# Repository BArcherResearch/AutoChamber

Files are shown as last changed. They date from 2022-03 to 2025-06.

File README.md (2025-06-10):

# AutoChamber 

Follow "AutoChamber/Chamber_1/Build_Guide/Chamber.1 Build guide" to find the chamber build guide.

## Building an open-source community around the development and application of automatically ventilating floating greenhouse gas flux chambers. 

My name is ***** and I am currently a doctoral candidate working with *********

My research focus is greenhouse gas dynamics from freshwater bodies. In particular, the development of opensource technical solutions for the collection of GHG flux data over higher temporal and spatial resolutions than has typically been achievable with floating chamber methods, or without extensive engineering experience. 

The goal of this project is to provide all the information required for people, even those with little to no experience in 3d printing or the arduino environment, to be able to build a standardised automatically ventilating floating chamber system, capable of collecting GHG flux data of a quality suitable for publication. 

In doing so, the project aims to enhance the resolution of the global freshwater GHG budget by offering a solution that aligns with the philosophy and popularity of the floating chamber method—being low-cost, easily transportable and deployable, and requiring minimal construction skills.

By using 3d printing and universally available parts, the system aims to be standardised between research groups, eliminating the time investment, engineering skills and unrepeatability that often come with lab builds.

Developing the optimal system for these grand goals is an iterative and collaborative process. But with the release of "Chamber_1" as a part of my doctoral thesis, I hope to inspire the community and conversation around automatically ventilating chamber standardisation, and provide a case for what openSource science can achieve. 

## A note for those anxious about the 3d printing element of this project

If there is enough interest in the "Chamber_1" design or future designs/iterations, 3d printing (and thus subsequent post printing epoxy sealing steps) could be avoided or reduced by investing in injection moulding moulds and providing some of the parts as a kit; for example the main body and lid. 

This approach has been employed successfully by other opensource projects such as the "snowcat" by rctestflight (https://www.kickstarter.com/projects/164488684/r-c-snowcat-tracks-rctestflight). Not only does this approach save lots of time that would otherwise be taken by printing, but also it reducing the cost of the individual parts (after the moulds have been funded of course) and ensuring the gas tight nature of the design. 

In the mean time, the cost of 3d printing has been taken into account by basing the build of Chamber_1 around the most economic FDM style printer available on the market at the time of publication, the **anycubic chiron**.

Additionally, the rise of consumer based 3d printers means that many universities and Maker spaces now have 3d printing facilities that students can utilise.

However if this is still not a possibility or to your taste, low cost **3d printing services** are now offered by external companies such as JLCpcb. By simply providing the projects stl files, you can have your parts printed and delivered.

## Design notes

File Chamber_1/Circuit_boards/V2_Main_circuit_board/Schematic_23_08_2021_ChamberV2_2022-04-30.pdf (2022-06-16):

A | A
B | B
C | C
D | D
E | E
F | F
G | G
H | H

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
TITLE: Automatic GHG Chamber schematic version 2
REV: 1.0

Date: 23-08-2021

Sheet: 1/1
Drawn By:

Company: IGB-Berlin

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
GND GND

GND

10K

R14

1K for Q3 or 2.2k for Q15
R20

1K

R21

10K

R22

100nF

C5

100nF

C6

22pF

C7 | 22pF C8

SN74HC595DR

U7

QB 1
QC 2
QD 3
QE 4
QF 5
QG 6
QH 7
GND 8 | QH# 9

SRCLR# 10 SRCLK 11 RCLK 12 OE# 13 SER 14 QA 15 VCC 16

SN74HC595DR

U8

QB 1
QC 2
QD 3
QE 4
QF 5
QG 6
QH 7
GND 8 | QH# 9

SRCLR# 10 SRCLK 11 RCLK 12 OE# 13 SER 14 QA 15 VCC 16

MMBT2222A_C400799

Q1

+5V

MMBT2222A_C400799

Q3 | GND

PD6

Servo Connector

Optical interrupt Connector

+5V

1K

R24

MMBT2222A_C400799

Q4
GND

GND

Fan Connector

1K

R25

MMBT2222A_C400799

Q5

GND

+5V

1K

R26

MMBT2222A_C400799

Q6

GND

SCL

SDA

SCL

SDA

HC-12 connection with switch

1K

R27
+5V

MMBT2222A_C400799
Q7

GND

Sensor Board Connection

HC-12

HC-12

DS1307Z+T&R

U5

X1

1

X2

2 VBAT

3

GND

4

SDA

5

SCL

6 | SQWOUT

7

VCC

8

SCL
SDA
32.768KHz

X3

GND

+5V

+5V

100nF

C9 CR2032-BS-6-1

B1

1 2

GND

Real Time Clock

TXB0104QPWRQ1

U9
VCCA

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
7 OE

8 NC

9 B4 10 B3 11 B2 12 B1 13 VCCB 14

+3V

+3V

100K

R31

100K

R32

+3V

+3V

GND

100K

R33

SD card reader

Ben Archer

24v power connector (from external 5amp boost converter)

Board power 5v connector

GND

MMBT2222A_C400799

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
AMS1117-3.3_C369933

U2

GND/ADJ

1
Output

2
Input

3

Output

4

GND

100nF +3V

C1

100nF

C2

-24v

19-217/BHC-ZL1M2RY/3T

LED1

FC-2012HRK-620D

LED4

19-217/GHC-YR1S2/3T

LED2

19-213/Y2C-CQ2R2L/3T(CY)

LED3

TS-1187A-B-A-B

SW2

2 1

4

3

4.7K

R29
4.7K

R30

16MHz

X2

4

1 | 2
| 3
GND
GND

HYC77-TF09-200

CARD1

DAT2

1
CD/DAT3

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
DAT0

7
DAT1

8
CD
9 | 10

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
Editing notes:
1. Removed switches and the spare sensor board connections

Shift register 1 (pins 0-7)

Shift register 2 (pins 8-15)

2. Removed L293D stepper driver

Shift register 3 (pins 16-23)

SN74HC595DR

U1

QB 1
QC 2
QD 3
QE 4
QF 5
QG 6
QH 7
GND 8 | QH# 9
SRCLR# 10 SRCLK 11 RCLK 12 OE# 13 SER 14 QA 15 VCC 16 | +5V

+5V

GND

GND

3. Added 3rd shift register (Just incase more pins are needed in the future).
4. Removed boost convertor circuit

B5B-XH-A (LF)(SN)

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
B4B-XH-A(LF)(SN)

U4

Red

1 Blue

2 Black

3 Green

4

B3B-XH-A(LF)(SN)

U10

1

1

2

2

3

3

B3B-XH-A(LF)(SN)

U12

1

1

2

2

3

3

B2B-XH-A (LF)(SN)

CN2

-5v

1

+5v

2

B2B-XH-A (LF)(SN)

CN3

1

1

2

2

GND

+5V

Programming port

B2B-XH-A (LF)(SN)

CN5

1

1

2

2

5. Removed the ICSP header pins, because I never used them on the V1. For most of the reprogramming I just removed the ATMEGA and re_burned the bootloader on the bootloader programming shield that I have
6. Converted the dupont connection points to JST type (JST sales America)
7. Removed 28BYJ-48 connector

65nm Nema 48 stepper motor connection

ZIFSOCKET-28-3ZIFFSOCKET-28-3

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
P$10

10

P$11

| 11 12 13

PD6

P$12

P$13

P$14

14 | P$15

15

P$16

16

P$17

17

P$18

18

P$19

19

P$20

20

P$21

21

P$22

22

P$23

23

P$24

24

P$25

25

P$26

26

P$27

27

P$28

28

atmega328p zif socket

TMC2208
VMOT 16 GND 15 M1B 14 M1A 13 M2A 12 M2B 11 VIO 10 GND 9 | DIR 8
STEP 7
CLK 6
PDN 5
UART 4
MS2 3
MS1 2
EN 1

SS310_C513470
D1

SS310_C513470

D2

SS310_C513470
D6
8. Added the zif 24 pin socket in place of the atmega. This will need to be ordered from mouser rather than lcsc electronics...unless I can find one
9. Added socket for TMC2208 motor driver shield. This MUST be a removable shield because it is a part that can break regularly
10. Added the schematic for the Watterott electronics StepSTick-protector V2 SS³¹⁰_C⁵¹³⁴⁷⁰

D10

SS310_C513470
D11

SS310_C513470

D12

SS310_C513470

D13SS³¹⁰_C⁵¹³⁴⁷⁰

D14

GND

VMOT

SS310_C513470

D3

10uF

C3

(a) 2 exposed copper pads that can be connected to enable the spread cycle on tmc2100 stepper drivers

(a)

GND

SRD-5VDC-SL-A

K3

2

1 | 4
3 | MMBT2222A_C400799

Q9

1K

R18

Relay_1

+5V

GND

1N4007

D4

1000uF

C15

GND

-24v

+24v

1N4007

D5

GND

+5V

Relay_2

1K

R6

MMBT2222A_C400799

Q10

SRD-5VDC-SL-A

K1

2

1 | 4
| 3

Stepper motor power control

Peristaltic pump motor control

+24v

+24v B2B-XH-A (LF)(SN)

CN6

-5v 1

+5v 2
-24v

Peristaltic pump connector

HX711 Load Cell 1

B4B-XH-A(LF)(SN)

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
B4B-XH-A(LF)(SN)

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
HX711 Load Cell 2

GND | GND

LC1_SCK

LC2_SCK

LC1_DT

LC2_DT

LC1_SCK

LC1_DT

. Step

Step

11. Added relays
12. Change the connections for the shift registers
13. Added ferrite bead

Straight-through

L1
Ferrite bead impedance: 21 Ohm @ 10 MHz

MMBT2222A_C400799

Q11

+5V

1K

R7

LC V+

. DIR

MS1

MS2

DIR
EN..
MS2 | MS1

Relay_2

LC V+

LC2_DT

Relay_1

LC2_SCK

CH4_2
CH4_3
CH4_4

CH4_1

Added CH4 power connector

CH4_2

MMBT2222A_C400799

Q12

1K

R8
CH4_3

MMBT2222A_C400799

Q13

1K

R9
CH4_4

MMBT2222A_C400799

Q14

1K

R10

14. Wired up the added shift register to include the individual methane sensors and moved any switching pins from the atmega to this shift register, to make space for additional load cell
16. Wired the right colour wire to the right output from the stepper motor

74AHC1GU04GW-Q100H

U15

NC 1

A

2

GND 3
Y

4

VCC 5

EN

+5V

GND

Single inverter Logic gate

15. Added a single NOT inverter logic gate, where I had a 6x IC logic gate on the perf board. This is more sensible in terms of space
17. 2 options for Optical input...the electrics on the main board connector for 4 wired, and the old style connector (with electronics on seperate board) just incase

180

R11

2.2K

R12

B4B-XH-A(LF)(SN)

U16

D+..

1

D-

2

E+

3

E-

4

Photo interrupter

+5V

GND

GND

+5V

Photointerrupter_Signal

Photointerrupter_Signal

18. reverse voltage protection efuse for just the arduino and electronics control. The heavier stuff run away from it because the efuse I have is only up to 1.6 amps, the 2amp version is not available
19. microusb powering option for 5v

MICRO5.9MMUSB

USB1

VBUS

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
TPS25921ADR

U17

GND

1
SS

2
ENUV

3
IN
4 | OUT

5

#FLT

6

ILIM

7

OVP

8

470K

R13

215K

R15

169K

R16

1nF

C4

210K

R17

Unspecified

R19

100uf

C10

0.1uf

C11

Microcontroller circuit protection (b)

(b) All control components are through hole to allow later changes to values. Incase the circuit does not work, or components are not available, I have included copper pads to be soldered to the circuit to be used. If no circuit protector is used, be cautious.

LTV-816S-TA1-C

U18

AN

1

CAT

2 EM

3

COL

4

30

R23

MICRO5.9MMUSB

USB2

VBUS

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
B2B-XH-A (LF)(SN)

CN7

-5v (2)

1

+5v (2)

2

GND
Motor battery pulse

Motor battery pulse

B2B-XH-A (LF)(SN)

CN8

-5v (2)

1

+5v (2)

2

Motor battery power 5v in

Motor battery power 5v out (to 5amp boost converter)

+5V

+5V

5v no efuse

5v no efuse

5v no efuse

5v no efuse

5v no efuse

5v no efuse

B5B-XH-A (LF)(SN)

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
CH4_1

MMBT2222A_C400799

Q8
+5V

1K

R28

B4B-XH-A(LF)(SN)

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
Power on pulse main system

30

R35

Power on pulse main system GND

HDR-F-2.54_1x5

H1

1

2

3

4

5

main power pulse

main power pulse

- 2oz copper pcb. All 5v traces 0.3mm (1.65 amps), other than the servo which should be higher if possible (0.684mm for 3amps). All 24v traces 1.38mm (5amps)

1N4007

D7

TIP120

Q15

GND

Mosfet_1

Mosfet_1

5v no efuse
Mosfet

Mosfet or Transistor
Power switcihing options

SI4599DY

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
4 D2

5

D2

6

D1

7

D1

8

Motor battery lipo voltage monitoring circuit option

4.7K

R34

24K

R36

Motor_Voltage

motor_lipo_voltage

100K

R37

GND

GND

100K

R38

GND

motor_5v_in

motor_5v_in

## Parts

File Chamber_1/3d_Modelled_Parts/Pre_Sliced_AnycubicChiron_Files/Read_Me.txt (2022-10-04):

Pre-sliced flies for Anycubic Chiron

The purpose of these files is to provide a "plug and play" option for those who would like to use the Anycubic Chiron to build their chambers. 

Simply copy the files onto a USB stick, and press print! No slicing required. 

"All parts together..." files represent the fastest method of printing for mass chamber production. HOWEVER, please consider that when printing many parts
at the same time, you can also loose many parts at the same time if printing errors are experienced. 

Single part options are perfect files to print when only one part is required. For example, if a part has been damaged in the field or during 
construction, a new one can be quickly printed and re-installed. 

This selection of files were sliced using Ultimaker Cura 4.11.0.

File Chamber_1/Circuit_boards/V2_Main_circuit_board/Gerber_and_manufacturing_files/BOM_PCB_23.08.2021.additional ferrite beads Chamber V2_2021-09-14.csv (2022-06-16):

ID | Name | Designator | Footprint | Quantity | Manufacturer Part | Manufacturer | Supplier | Supplier Part | Price | Pins | 3DModel | JLCPCB Part Class | LCSC Assembly | Capacitance | Contributor | Frequency | SMT Type | description | image | link
1 | 100nF | C1,C2,C5,C6,C9 | C0603 | 5 | GRM188R11H104KA93D | MuRata | LCSC | C86009 | 0.02 | 2 | C0603_L1.6-W0.8-H0.8 |  |  |  | layout |  |  |  |  | https://item.szlcsc.com/362304.html
2 | CAP-TH_BD10.0-P5.00-D1.0-FD | REF2 | CAP-TH_BD10.0-P5.00-D1.0-FD | 1 | 01EC4294SHC1000UF25V | KNSCHA | LCSC | C503217 | 0.06 | 2 | CAP-TH_D10.0-H16.0-P5.00 | Extended Part |  | 1000uF | 官方封装库 |  |  |  |  | https://item.szlcsc.com/44833.html
3 | UQFN-12_L2.0-W1.7-P0.40-BL | U21 | UQFN-12_L2.0-W1.7-P0.40-BL | 1 | TXB0104RUTR | TI | LCSC | C105266 | 0.803 | 12 | UQFN-12_L2.0-W1.7-H0.5-P0.40 | Extended Part |  |  | 立创EDA官方封装库 |  |  |  |  | https://atta.szlcsc.com/upload/public/pdf/source/20210803/C604193_D56294ACCFB5230BC8793C49C7DABAEA.pdf
4 | SOT-223-4_L6.5-W3.5-P2.30-LS7.0-BR | REF1 | SOT-223-4_L6.5-W3.5-P2.30-LS7.0-BR | 1 | AMS1117-3.3V | WPMtek(维攀微) | LCSC | C2688239 | 0.093 | 4 | SOT-223-4P_L6.5-W3.5-H1.6-LS7.0-P2.30 | Extended Part |  |  | 立创EDA官方封装库 |  |  |  |  | https://item.szlcsc.com/84517.html
5 | CRYSTAL-SMD_4P-L3.2-W2.5-BL | X1 | CRYSTAL-SMD_4P-L3.2-W2.5-BL | 1 | X1E0000210375000G | EPSON | LCSC | C89379 | 0.183 | 4 | OSC-SMD_4P-L3.2-W2.5-H1.0 | Extended Part |  |  | 立创EDA官方封装库 | 16MHz |  |  |  | https://item.szlcsc.com/15866.html
6 | SOT-23-5_L3.0-W1.7-P0.95-LS2.8-BR | U14 | SOT-23-5_L3.0-W1.7-P0.95-LS2.8-BR | 1 | SN74LVC1G04DBVR | TI | LCSC | C7827 | 0.066 | 5 | SOT-23-5_L2.9-W1.6-H1.1-LS2.8-P0.95 | Extended Part |  |  | 87804271zpf |  |  |  |  | https://item.szlcsc.com/236104.html
7 | CONN-TH_5P-P2.50_XH-5A_C2318 | CN4,CN10 | CONN-TH_5P-P2.50_XH-5A_C2318 | 2 | XH-5A | BOOMELE | LCSC | C2318 | 0.012 | 5 | XH2.5-5A | Extended Part |  |  | 立创EDA官方封装库 |  |  |  |  | https://item.szlcsc.com/2692.html
8 | TO-220-3_L10.0-W4.5-P2.54-L | U19 | TO-220-3_L10.0-W4.5-P2.54-L | 1 | TIP120 | STMicroelectronics | LCSC | C262990 | 0.6 | 3 | TO-220-3_L10.0-W4.5-P2.54-L | Extended Part |  |  | 87804271zpf |  |  |  |  | https://item.szlcsc.com/233115.html
9 | 1K | R20,R34,R36,R38,R37 | RES-TH_BD2.4-L6.3-P10.30-D0.6 | 5 |  |  |  |  |  | 2
10 | SO-8_L4.9-W3.9-P1.27-LS5.9-BL | U17 | SO-8_L4.9-W3.9-P1.27-LS5.9-BL | 1 | SI4599DY | VBsemi Elec | LCSC | C725174 | 0.636 | 8 | SO-8_L4.9-W3.9-H1.5-LS5.9-P1.27 | Extended Part |  |  | 官方封装库 |  |  |  |  | https://item.szlcsc.com/232656.html
11 | 1N4007 | D15,D4,D5 | DO-41_BD2.4-L4.7-P8.70-D0.9-RD | 3 | 1N4007 | SEMTECH | LCSC | C106903 | 0.015 | 2 | DO-41_D2.4-L4.7-P8.70 |  |  |  | 官方封装库 |  |  |  |  | https://item.szlcsc.com/85412.html
12 | CR2032-BS-6-1 | B1 | BAT-TH_CR2032-BS-6-1 | 1 | CR2032-BS-6-1 | Q&J | LCSC | C70377 | 0.173 | 2 | BAT-SMD_L28.5-W16.0-H5.5-LS31.3_CR2032-BS-6-1 |  | Yes |  | 立创EDA官方封装库 |  | Extend |  | //image.lceda.cn/szlcsc/C70377.jpg | https://item.szlcsc.com/71472.html
13 | 10uF | C3 | C1206 | 1 | CL31A106KBHNNNE | SAMSUNG | LCSC | C13585 | 0.039 | 2 | C1206_L3.2-W1.6-H1.3 | Basic Part |  |  | layout |  |  |  |  | https://item.szlcsc.com/89171.html
14 | 22pF | C7,C8 | C0603 | 2 | GRM1882C1H220JA01D | MuRata | LCSC | C85969 | 0.005 | 2 | C0603_L1.6-W0.8-H0.8 |  |  |  | layout |  |  |  |  | https://item.szlcsc.com/362304.html
15 | HYC77-TF09-200 | CARD1 | TF-SMD_HYC77-TF09-200 | 1 | HYC77-TF09-200 | 华宇创 | LCSC | C341092 | 0.143 | 13 | TF-SMD_HYC77-TF09-200 |  |  |  | 官方封装库 |  |  |  |  | https://item.szlcsc.com/318320.html
16 | B2B-XH-A (LF)(SN) | CN2,CN3,CN5,CN6,CN7,CN8 | CONN-TH_B2B-XH-A-LF-SN | 6 | - | JST Sales America | LCSC | C158012 | 0.028 | 2 | XH2.5-2A | Extended Part |  |  | 立创EDA官方封装库
17 | SS310_C513470 | D1,D2,D3,D6,D10,D11,D12,D13,D14 | SMA_L4.3-W2.6-LS5.2-RD | 9 | SS310 | Slkor(SLKORMICRO Elec.) | LCSC | C513470 | 0.074 | 2 | SMA_L4.3-W2.6-LS5.2-RD | Extended Part |  |  | 官方封装库 |  |  |  |  | https://item.szlcsc.com/34721.html
18 | SRD-5VDC-SL-A | K1,K3 | RELAY-TH_SRD-XXVDC-XX-A | 2 | SRD-5VDC-SL-A | Ningbo Songle Relay | LCSC | C140615 | 0.365 | 4 | RELAY-TH_L19.2-W15.6-H15.8-A |  |  |  | 官方封装库 |  |  |  |  | https://item.szlcsc.com/94914.html
19 | Straight-through | L1 | BEAD-TH_BD3.5-L6.0-P10.00-D0.9 | 1 | Straight-through beads | ML | LCSC | C46030 | 0.008 | 2 | BEAD-TH_D3.5-L6.0-P10.2 | Extended Part |  |  | 官方封装库 |  |  |  |  | https://item.szlcsc.com/47033.html
20 | 19-217/BHC-ZL1M2RY/3T | LED1 | LED0603-R-RD | 1 | 19-217/BHC-ZL1M2RY/3T | EVERLIGHT | LCSC | C72041 | 0.016 | 2 | LED0603_Green |  | Yes |  | 官方封装库 |  | Basic |  | //image.lceda.cn/szlcsc/C72041.jpg | https://lcsc.com/product-detail/Light-Emitting-Diodes-LED_Hubei-KENTO-Elec-0603-Green_C12624.html
21 | 19-217/GHC-YR1S2/3T | LED2 | LED0603-R-RD | 1 | 19-217/GHC-YR1S2/3T | EVERLIGHT | LCSC | C72043 | 0.025 | 2 | LED0603_Green |  | Yes |  | 官方封装库 |  | Basic |  | //image.lceda.cn/szlcsc/C72043.jpg | https://lcsc.com/product-detail/Light-Emitting-Diodes-LED_Hubei-KENTO-Elec-0603-Green_C12624.html
22 | 19-213/Y2C-CQ2R2L/3T(CY) | LED3 | LED0603-R-RD | 1 | 19-213/Y2C-CQ2R2L/3T(CY) | EVERLIGHT | LCSC | C72038 | 0.019 | 2 | LED0603_Green |  | Yes |  | 官方封装库 |  | Basic |  | //image.lceda.cn/szlcsc/C72038.jpg | https://lcsc.com/product-detail/Light-Emitting-Diodes-LED_Hubei-KENTO-Elec-0603-Green_C12624.html
23 | FC-2012HRK-620D | LED4 | LED0805-RD | 1 | FC-2012HRK-620D | NATIONSTAR | LCSC | C84256 | 0.012 | 2 | LED0805_Green |  | Yes |  | layout |  | Basic |  | //image.lceda.cn/szlcsc/C84256.jpg | https://item.szlcsc.com/255094.html
24 | TMC2208 | NO | TMC2208_SILENTSTEPSTICK_EVAL_BRD | 1 | TRINAMIC |  | Farnell | 2822166 |  | 16 |  |  |  |  | andyfierman |  |  |  |  | https://uk.farnell.com/trinamic/tmc2208-silentstepstick/stepper-driver-board-2-phase-motor/dp/2822166
25 | MMBT2222A_C400799 | Q1,Q2,Q3,Q4,Q5,Q6,Q7,Q8,Q9,Q10,Q11,Q12,Q13,Q14 | SOT-23-3_L3.0-W1.7-P0.95-LS2.9-BR | 14 | MMBT2222A | SLKORMICRO Elec. | LCSC | C400799 | 0.016 | 3 | SOT-23-3L_L2.9-W1.6-H1.1-LS2.8-P0.95 |  | Yes |  | 87804271zpf |  | Extend |  |  | https://item.szlcsc.com/139341.html
26 | 1K | R1,R2,R3,R4,R5,R6,R7,R8,R9,R10,R18,R21,R24,R25,R26,R27,R28 | R0603 | 17 | ESR03EZPJ102 | ROHM Semicon | LCSC | C253329 | 0.014 | 2 | R0603_L1.6-W0.8-H0.8 |  |  |  | layout |  |  |  |  | https://item.szlcsc.com/137208.html
27 | 180 | R11 | R1206 | 1 | 1206W4F1800T5E | UniOhm | LCSC | C17924 | 0.004 | 2 | R1206_L3.2-W1.6-H0.6 | Basic Part |  |  | layout |  |  |  |  | https://item.szlcsc.com/311874.html
28 | 2.2K | R12 | R0603 | 1 | 0603WAF2201T5E | UniOhm | LCSC | C4190 | 0.001 | 2 | R0603_L1.6-W0.8-H0.8 | Basic Part |  |  | 立创EDA官方封装库 |  |  |  |  | https://www.mouser.in/datasheet/2/447/PYu_RT_1_to_0_01_RoHS_L_11-1669912.pdf
29 | 10K | R14,R22 | R0603 | 2 | 060300J0103T5E | UniOhm | LCSC | C149496 | 0.002 | 2 | R0603_L1.6-W0.8-H0.8 |  |  |  | layout |  |  |  |  | https://item.szlcsc.com/137208.html
30 | 30 | R23,R35 | RES-TH_BD4.5-L11.5-P15.50-D0.7 | 2 | MFR01SF300JA10 | UniOhm | LCSC | C58702 | 0.015 | 2 | RES-TH_BD4.5-L11.5-P15.50 | Extended Part |  |  | 官方封装库 |  |  |  |  | https://item.szlcsc.com/62379.html
31 | 4.7K | R29,R30 | R1206 | 2 | 1206W4F4701T5E | UniOhm | LCSC | C17936 | 0.004 | 2 | R1206_L3.2-W1.6-H0.6 |  | Yes |  | layout |  | Basic |  |  | https://item.szlcsc.com/311874.html
32 | 100K | R31,R32,R33 | R1206 | 3 | RMC1206100K5%N | Tyohm | LCSC | C269750 | 0.006 | 2 | R1206_L3.2-W1.6-H0.6 |  |  |  | layout |  |  |  |  | https://item.szlcsc.com/311874.html
33 | TS-1187A-B-A-B | SW2 | SW-SMD_4P-L5.1-W5.1-P3.70-LS6.4 | 1 | TS-1187A-B-A-B | XKB Enterprise | LCSC | C318884 | 0.014 | 4 | SMD-SW_4P-L5.1-W5.1-H3.5-LS6.4-P3.70 |  | Yes |  | LCSC |  | Extend |  |  | https://item.szlcsc.com/299977.html
34 | SN74HC595DR | U1,U7,U8 | SOIC-16_L9.9-W3.9-P1.27-LS6.0-BL | 3 | SN74HC595DR | TI | LCSC | C10092 | 0.232 | 16 | SOIC-16_L9.9-W3.9-H1.8-LS6.0-P1.27 |  | Yes |  | 官方封装库 |  | Extend |  | //image.lceda.cn/szlcsc/C10092.jpg | https://item.szlcsc.com/241229.html
35 | B4B-XH-A(LF)(SN) | U3,U4,U6,U13,U16 | CONN-TH_B4B-XH-A-LF-SN | 5 | B4B-XH-A(LF)(SN) | JST Sales America | LCSC | C144395 | 0.045 | 4 | XH2.5-4A | Extended Part |  |  | 立创EDA官方封装库 |  |  |  |  | https://item.szlcsc.com/155727.html
36 | DS1307Z+T&R | U5 | SOIC-8_L5.0-W4.0-P1.27-LS6.0-BL | 1 | DS1307Z+T&R | MAXIM | LCSC | C9868 | 1.492 | 8 | SOIC-8_L4.9-W3.9-H1.7-LS6.0-P1.27 |  | Yes |  | 官方封装库 |  | Extend |  | //image.lceda.cn/szlcsc/C9868.jpg | https://item.szlcsc.com/417287.html
37 | B3B-XH-A(LF)(SN) | U10,U12 | CONN-TH_3P-P2.50_B3B-XH-A-LF-SN | 2 | B3B-XH-A(LF)(SN) | JST Sales America | LCSC | C144394 | 0.041 | 3 | CONN-TH_XH2.50-LI-3P | Extended Part |  |  | 立创EDA官方封装库 |  |  |  |  | https://lcsc.com/product-detail/Wire-To-Board-Wire-To-Wire-Connector_JST-Sales-America_B3B-XH-A-LF-SN_JST-Sales-America-B3B-XH-A-LF-SN_C144394.html
38 | ZIFSOCKET-28-3ZIFFSOCKET-28-3 | U11 | DIL28-3-ZIF_SOCKET | 1 |  |  |  |  |  | 28 |  |  |  |  | SparkFun |  |  | Lever-action ZIF socket for 28-pin ICs
39 | LTV-816S-TA1-C | U18 | SMD-4_L4.6-W6.5-P2.54-LS10.2-BL | 1 | LTV-816S-TA1-C | LITEON | LCSC | C115457 | 0.065 | 4 | SMD-4_L4.6-W6.5-H3.7-LS10.2-P2.54 | Extended Part |  |  | 立创EDA官方封装库 |  |  |  |  | https://item.szlcsc.com/67489.html
40 | MICRO5.9MMUSB | USB1,USB2 | MICRO-USB-SMD_5P-P0.65-H-F_MICRO5.9MMUSB | 2 | MICRO5.9mmusb | SHOU HAN | LCSC | C393940 | 0.029 | 11 | MICRO-USB-SMD_MICRO5.9MMUSB |  |  |  | 立创EDA官方封装库 |  |  |  |  | https://item.szlcsc.com/372552.html
41 | 32.768KHz | X3 | OSC-SMD_BD2.0-P2.54_TMXLI-206F 32.768KHZ 12.5PF 20PPM | 1 | TMXLi-206F32.768KHZ12PF10PPM | Zhejiang Abel Elec | LCSC | C164061 | 0.176 | 3 | OSC-SMD_BD2.0-P2.54_TMXLI-206F 32.768KHZ 12.5PF 20PPM |  |  |  | 立创EDA官方封装库
42 | HDR-F-2.54_1x5 | H1 | HDR-F-2.54_1X5 | 1 |  |  | LCSC | C50950 | 0.054 | 5 | HDR-F-2.54_1x5 |  |  |  | LCEDA_Lib
43 | BLM18HE152SZ1D | B1&2,BEAD2,BEAD3 | L0603 | 3 | BLM18HE152SZ1D | Murata Electronics | LCSC | C437403 | 0.054 | 2 | L0603_L1.6-W0.8-H0.5_BEAD | Extended Part |  |  | layout |  |  |  |  | https://item.szlcsc.com/344093.html

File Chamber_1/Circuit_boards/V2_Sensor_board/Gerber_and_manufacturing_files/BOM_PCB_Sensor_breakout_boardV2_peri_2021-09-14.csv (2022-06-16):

ID | Name | Designator | Footprint | Quantity | Manufacturer Part | Manufacturer | Supplier | Supplier Part | Price | Pins | 3DModel | JLCPCB Part Class | Capacitance | Contributor | link
1 | BLM18HE152SZ1D | BEAD1,BEAD2,BEAD3,BEAD4 | L0603 | 4 | BLM18HE152SZ1D | Murata Electronics | LCSC | C437403 | 0.054 | 2 | L0603_L1.6-W0.8-H0.5_BEAD | Extended Part |  | layout | https://item.szlcsc.com/344093.html
2 | 1000uF | C1 | CAP-TH_BD10.0-P5.00-D1.0-FD | 1 | RD1C108M10016PA | SAMWHA | LCSC | C160619 | 0.126 | 2 | CAP-TH_D10.0-H16.0-P5.00 |  |  | 官方封装库 | https://item.szlcsc.com/44833.html
3 | 1uF | C2,C3,C4,C5 | C0805 | 4 | CL21B105KBFNNNE | SAMSUNG | LCSC | C28323 | 0.01 | 2 | C0805_L2.0-W1.3-H1.3 | Basic Part |  | LCSC | https://item.szlcsc.com/373011.html
4 | XH-5A | CN1 | CONN-TH_5P-P2.50_XH-5A_C2318 | 1 | XH-5A | BOOMELE | LCSC | C2318 | 0.012 | 5 | XH2.5-5A | Extended Part |  | 立创EDA官方封装库 | https://item.szlcsc.com/2692.html
5 | 1N4007 | D1 | DO-41_BD2.4-L4.7-P8.70-D0.9-RD | 1 | 1N4007 | SEMTECH | LCSC | C106903 | 0.015 | 2 | DO-41_D2.4-L4.7-P8.70 |  |  | 官方封装库 | https://item.szlcsc.com/85412.html
6 | HDR-F-2.54_1x6 | H1,H2 | HDR-F-2.54_1X6 | 2 |  |  | LCSC | C40877 | 0.059 | 6 | HDR-F-2.54_1x6 |  |  | LCEDA_Lib
7 | HDR-F-2.54_1x5 | H3 | HDR-F-2.54_1X5 | 1 |  |  | LCSC | C50950 | 0.054 | 5 | HDR-F-2.54_1x5 |  |  | LCEDA_Lib
8 | KIP_HDR_F_-2.54_1x7 | P1,P2 | KIP_HDR_F_-11X1/2.54 | 2 | Female header 2.54-1*11P | BOOMELE | LCSC | C52709 | 0.098 | 7 |  |  |  | Jonatan Guerrero
9 | 3.3K | R1,R2,R3,R4 | RES-TH_BD2.2-L6.5-P10.50-D0.6 | 4 | MFR0W4F3301A50 | UniOhm | LCSC | C58610 | 0.008 | 2 | RES-TH_BD2.2-L6.5-P10.50 |  |  | 官方封装库 | https://item.szlcsc.com/59661.html
10 | 10K | R5,R6,R7,R8,R9,R10,R11,R12,R13,R14,R15,R16,R19,R20 | R1206 | 14 | RTT061002FTP | RALEC | LCSC | C104595 | 0.006 | 2 | R1206_L3.2-W1.6-H0.6 | Extended Part |  | layout | https://item.szlcsc.com/311874.html
11 | TGS2611 | U1,U4,U5,U6 | FIGARO-TGS2611 | 4 | TGS2600 | FIGARO |  |  |  | 4 |  |  |  | jasonmaher2308
12 | B4B-XH-A(LF)(SN) | U2,U3 | CONN-TH_B4B-XH-A-LF-SN | 2 | B4B-XH-A(LF)(SN) | JST Sales America | LCSC | C144395 | 0.045 | 4 | XH2.5-4A | Extended Part |  | 立创EDA官方封装库 | https://item.szlcsc.com/155727.html
13 | ADS1115IDGSR | U7,U8 | MSOP-10_L3.0-W3.0-P0.50-LS5.0-BL | 2 | ADS1115IDGSR | TI | LCSC | C37593 | 4.967 | 10 | MSOP-10_L3.0-W3.0-H1.1-LS5.0-P0.50 | Extended Part |  | 官方封装库 | https://item.szlcsc.com/221388.html
14 | TSSOP-24_L7.8-W4.4-P0.65-LS6.4-BL | U9 | TSSOP-24_L7.8-W4.4-P0.65-LS6.4-BL | 1 | TCA9548APWR | TI | LCSC | C130026 | 2.798 | 24 | TSSOP-24_L7.8-W4.4-H1.0-LS6.4-P0.65 | Extended Part |  | 官方封装库 | https://item.szlcsc.com/6601.html
15 | C1206 | C6 | C1206 | 1 | CL31A106KBHNNNE | SAMSUNG | LCSC | C13585 | 0.039 | 2 | C1206_L3.2-W1.6-H1.3 | Basic Part | 10uF | layout | https://item.szlcsc.com/89171.html

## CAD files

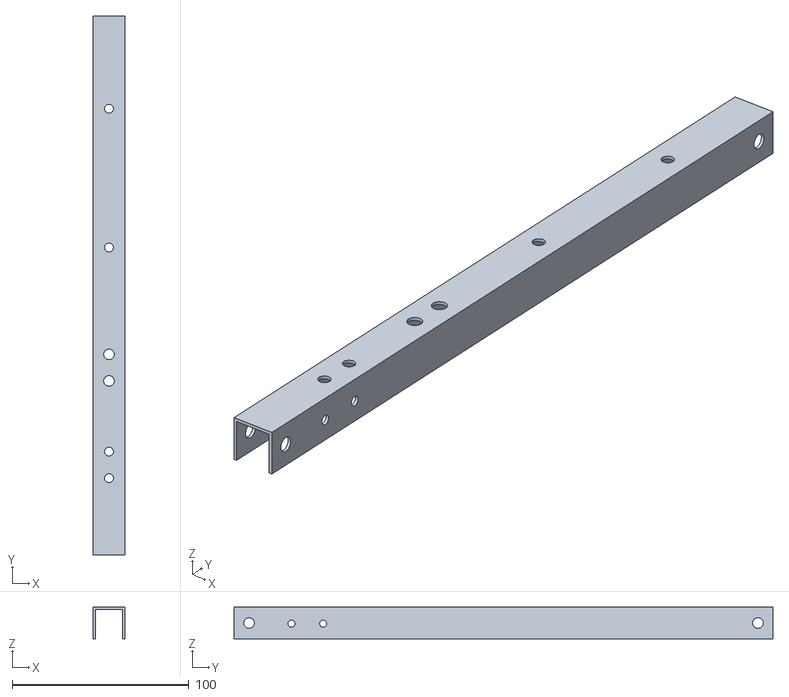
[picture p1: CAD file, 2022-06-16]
Chamber_1/3d_Modelled_Parts/3d_Files/Building_aids/Part_14_Aluminium_Bracket_Cut_Guide_27_04_2022.stl
18.0 x 305.0 x 18.0

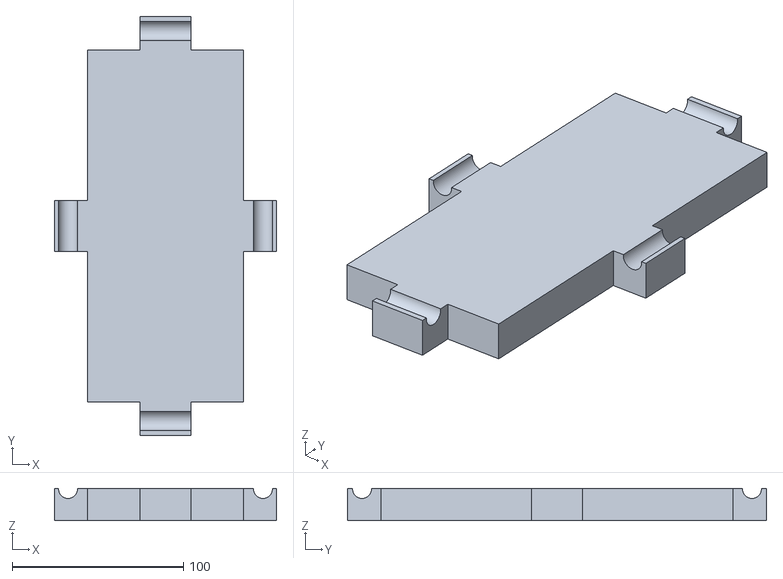
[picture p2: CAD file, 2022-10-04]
Chamber_1/3d_Modelled_Parts/3d_Files/Chamber_Parts/Part_10_Motor_case_lid_v13_05.10.2021.stl
130.0 x 245.0 x 19.0

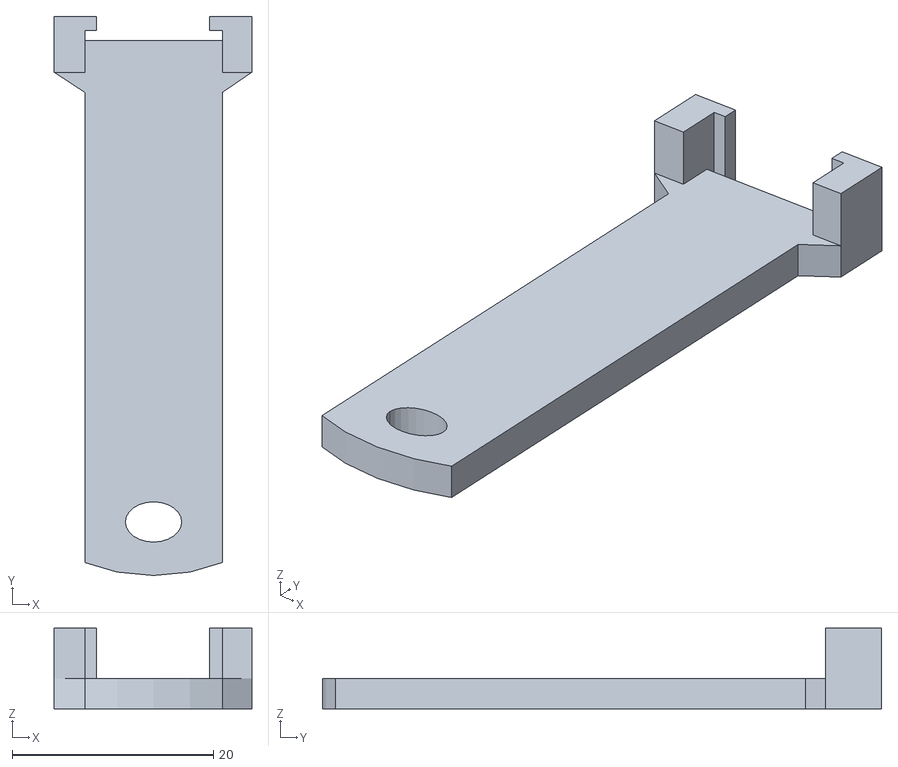
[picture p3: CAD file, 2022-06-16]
Chamber_1/3d_Modelled_Parts/3d_Files/Building_aids/Part_106_JST_puller_size_4.stl
19.6 x 55.5 x 8.00

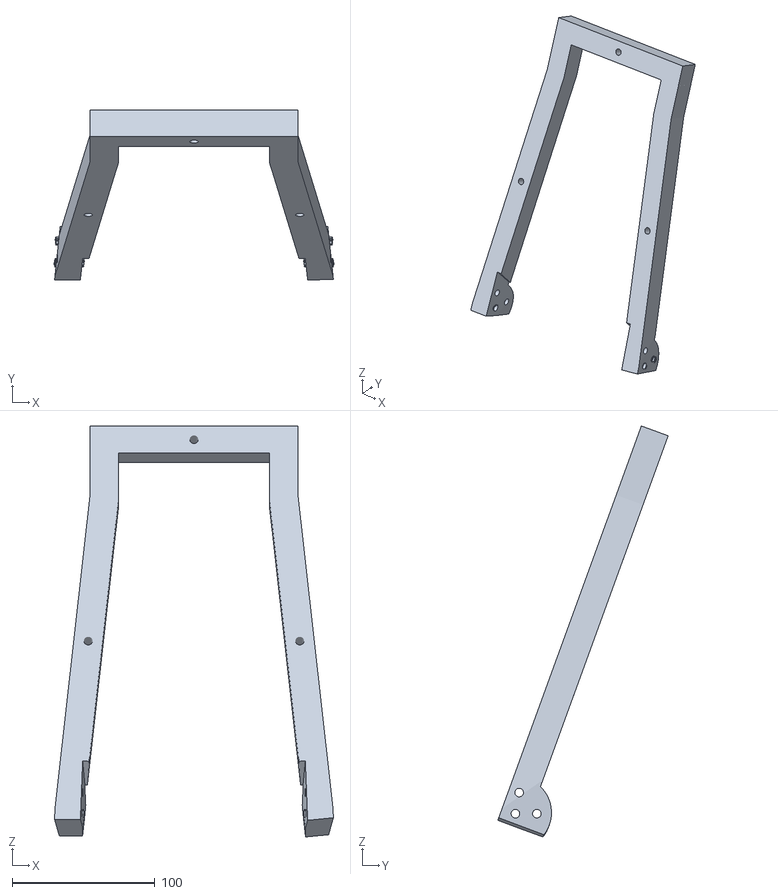
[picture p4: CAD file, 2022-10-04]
Chamber_1/3d_Modelled_Parts/3d_Files/Chamber_Parts/Part_3_Chamber_Float_Arm_v5_06.09.2022.stl
195.2 x 119.2 x 287.5

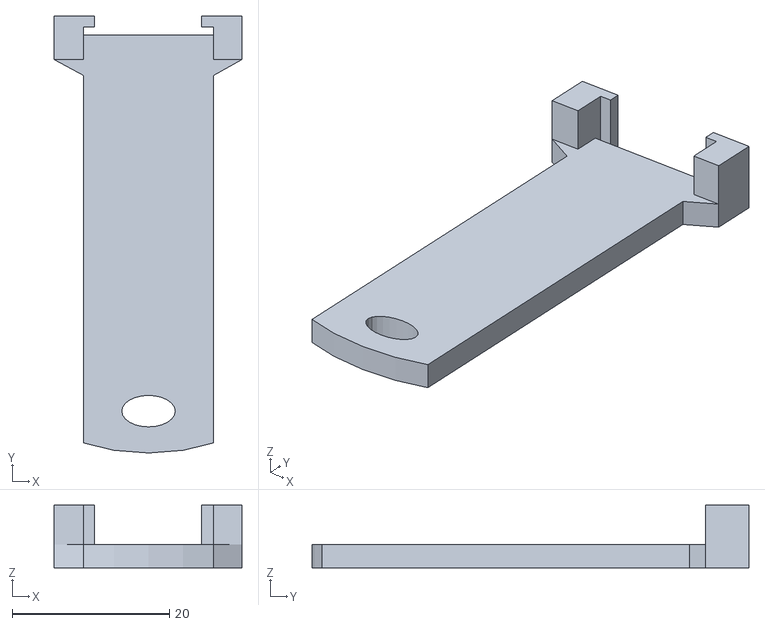
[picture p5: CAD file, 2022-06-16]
Chamber_1/3d_Modelled_Parts/3d_Files/Building_aids/Part_107_JST_puller_size_5.stl
23.8 x 55.5 x 8.00

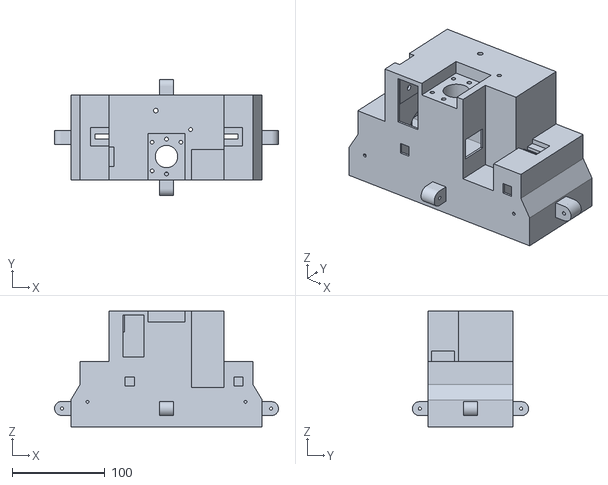
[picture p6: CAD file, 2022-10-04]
Chamber_1/3d_Modelled_Parts/3d_Files/Chamber_Parts/Part_9_Motor_Case_v15_21.08.2022.stl
241.0 x 125.0 x 124.8

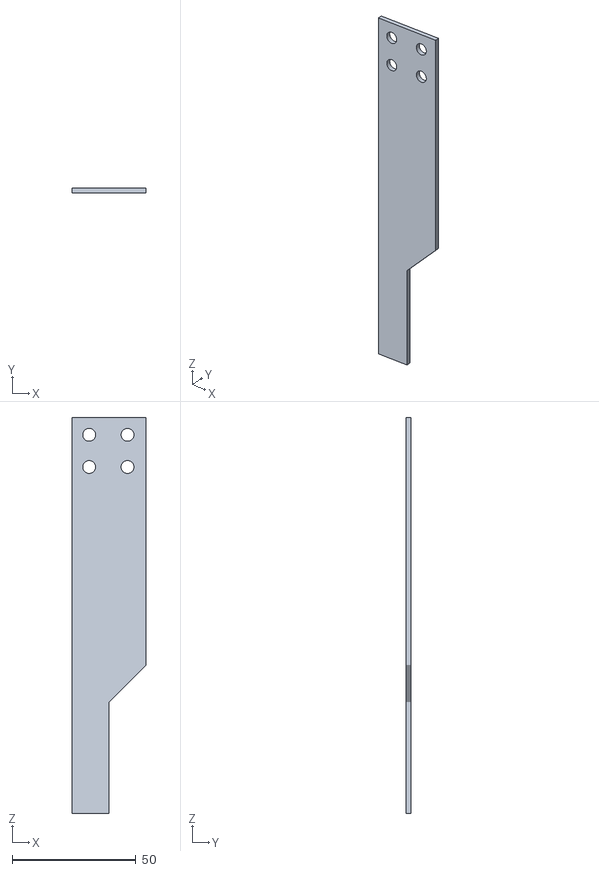
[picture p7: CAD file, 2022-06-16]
Chamber_1/3d_Modelled_Parts/3d_Files/Building_aids/Part_20_Lid_Optical_Interrupter_Template_28.04.2022.stl
30.0 x 2.00 x 160.0

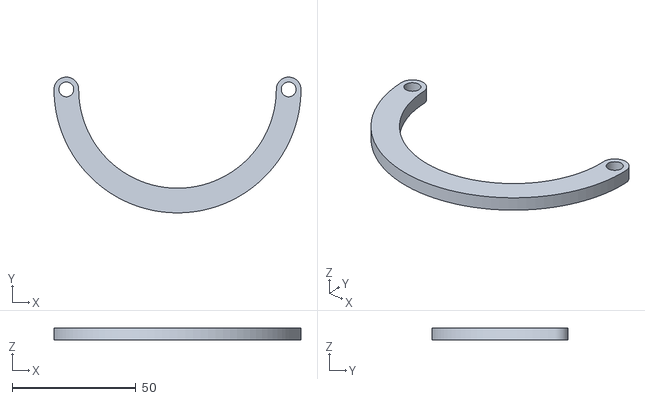
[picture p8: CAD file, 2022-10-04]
Chamber_1/3d_Modelled_Parts/3d_Files/Chamber_Parts/Part_7_Lid_arm_curved_03.02.2022.stl
100.0 x 55.0 x 5.00

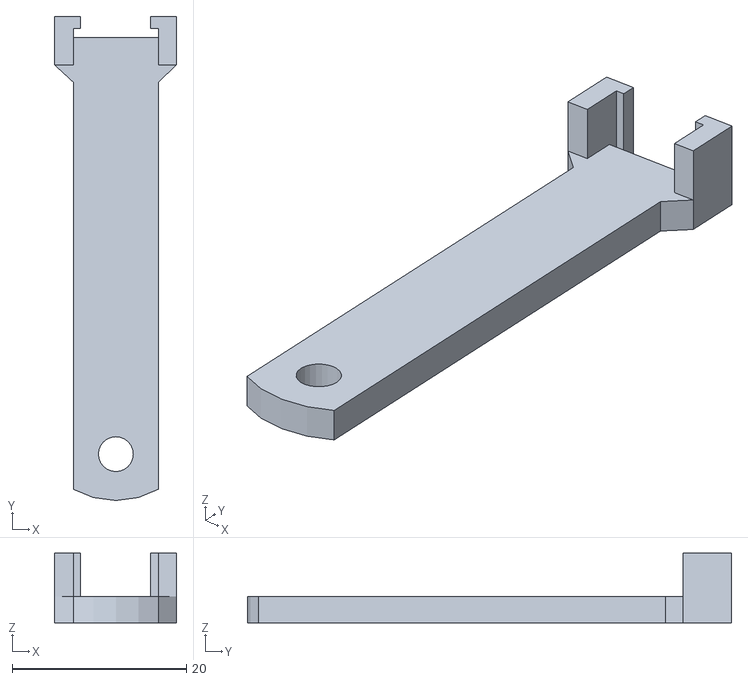
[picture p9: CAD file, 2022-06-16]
Chamber_1/3d_Modelled_Parts/3d_Files/Building_aids/Part_105_JST_puller_size_3.stl
14.0 x 55.5 x 8.00

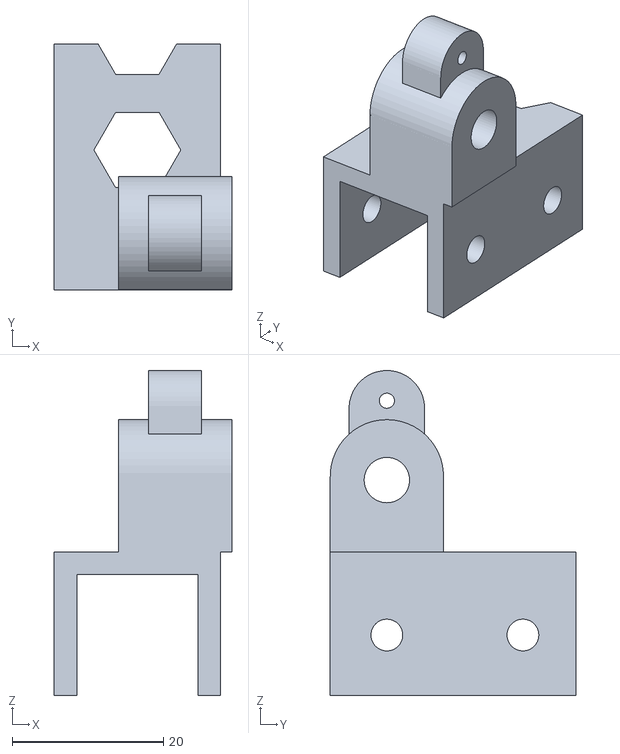
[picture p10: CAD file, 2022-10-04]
Chamber_1/3d_Modelled_Parts/3d_Files/Chamber_Parts/Part_6_a_Fan_Bracket_Left_20.07.2022.stl
23.5 x 32.5 x 43.0

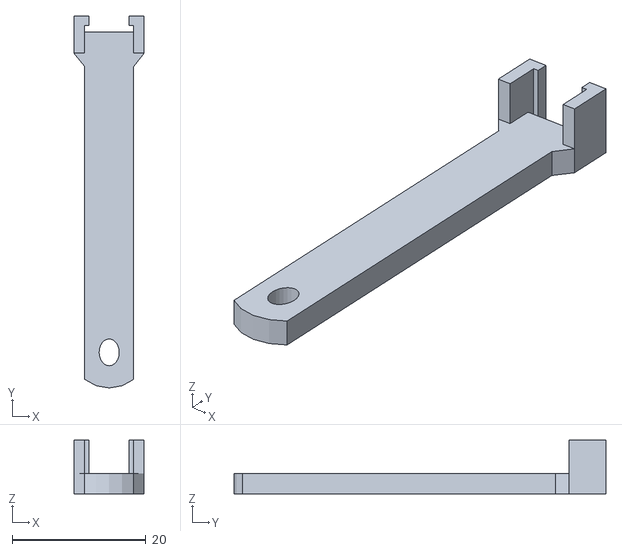
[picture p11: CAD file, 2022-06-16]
Chamber_1/3d_Modelled_Parts/3d_Files/Building_aids/Part_104_JST_puller_size_2.stl
10.5 x 55.5 x 8.00

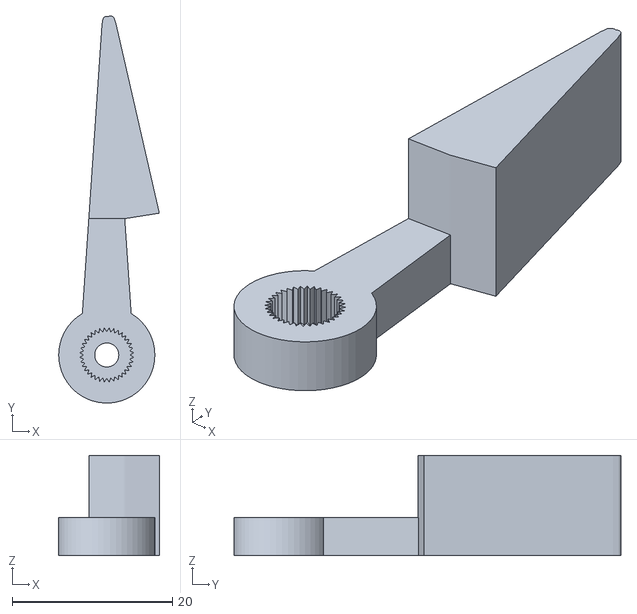
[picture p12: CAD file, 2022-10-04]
Chamber_1/3d_Modelled_Parts/3d_Files/Chamber_Parts/Part_19_Servo_Arm_13.05.2022.stl
12.6 x 48.3 x 12.5

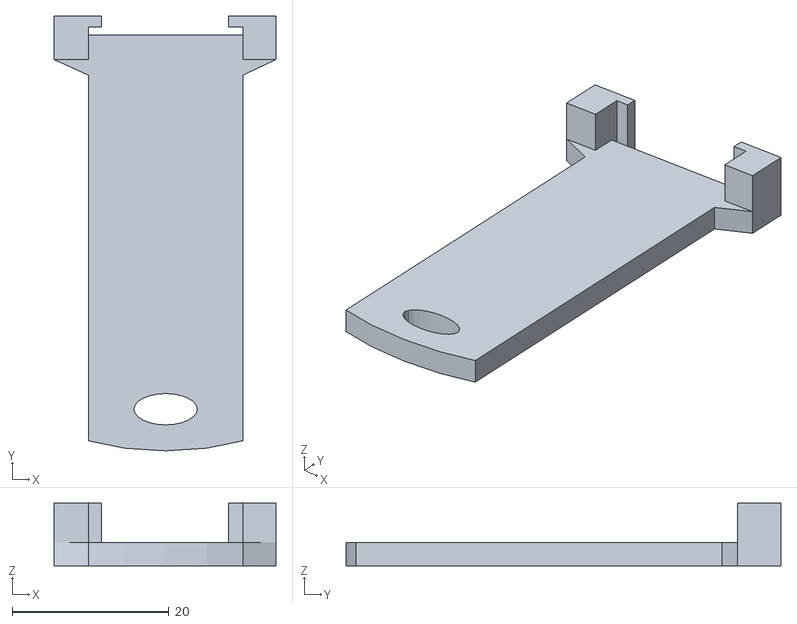
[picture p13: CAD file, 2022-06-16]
Chamber_1/3d_Modelled_Parts/3d_Files/Building_aids/Part_108_JST_puller_size_6.stl
28.4 x 55.5 x 8.00

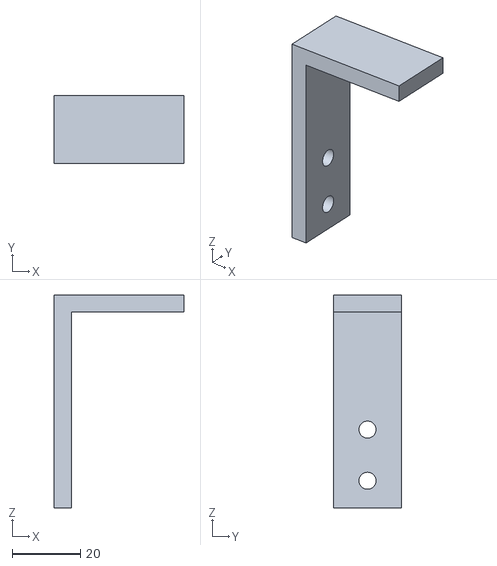
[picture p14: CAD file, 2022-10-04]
Chamber_1/3d_Modelled_Parts/3d_Files/Chamber_Parts/Part_9b_Pawl_guide_attachment_21.08.2022.stl
38.0 x 20.0 x 62.5

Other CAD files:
Chamber_1/3d_Modelled_Parts/3d_Files/Chamber_Parts/Part_3_Chamber_Float_Arm_v5_29.09.2022.stl
Chamber_1/3d_Modelled_Parts/3d_Files/Chamber_Parts/Part_6_b_Fan_Bracket_Right_20.07.2022.stl
Chamber_1/3d_Modelled_Parts/3d_Files/Chamber_Parts/Part_3.b_Chamber_Float_Arm_Tall_v5_06.09.2022.stl
Chamber_1/3d_Modelled_Parts/3d_Files/Chamber_Parts/Part_29_Chamber_Bottom_Cap V2 06.09.2021.stl
Chamber_1/3d_Modelled_Parts/3d_Files/Chamber_Parts/Part_1.b_Chamber_Body_Tall_23.01.2022.stl
Chamber_1/3d_Modelled_Parts/3d_Files/Chamber_Parts/Part_11_Motor_case_latch_small_27.07.2020.stl
Chamber_1/3d_Modelled_Parts/3d_Files/Chamber_Parts/Part_12_Motor_case_latch_large_04.07.2021.stl
Chamber_1/3d_Modelled_Parts/3d_Files/Chamber_Parts/Part_13_Motor_Case_Optical_Switch_06.11.2020.stl
Chamber_1/3d_Modelled_Parts/3d_Files/Chamber_Parts/Part_15_Bottom_Pawl_15.05.2022.stl
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

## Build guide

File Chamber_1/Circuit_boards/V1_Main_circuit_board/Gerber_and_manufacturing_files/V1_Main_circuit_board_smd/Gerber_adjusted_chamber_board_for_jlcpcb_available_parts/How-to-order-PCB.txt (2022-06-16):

How to Order PCB

Please refer to:
https://docs.easyeda.com/en/PCB/Order-PCB

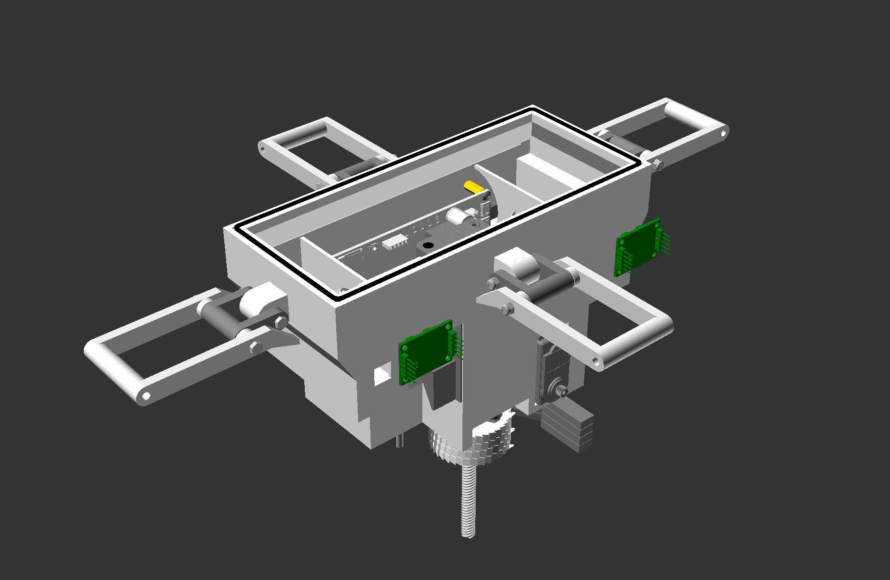
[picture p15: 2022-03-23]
Chamber_1/Build_Guide/Step 4_Construction_Manual_Animations/step_4b_5_animated.gif

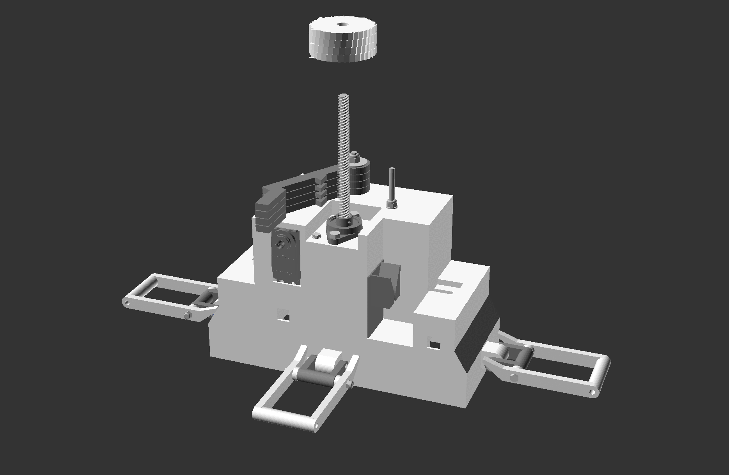
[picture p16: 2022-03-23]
Chamber_1/Build_Guide/Step 4_Construction_Manual_Animations/step_4b_3_animated.gif

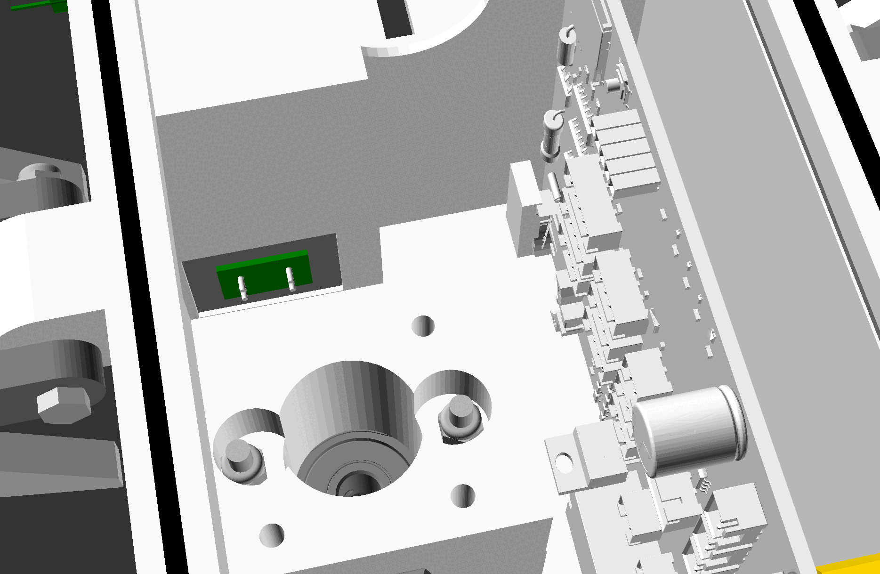
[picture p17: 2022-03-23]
Chamber_1/Build_Guide/Step 4_Construction_Manual_Animations/step_4b_9_animated.gif

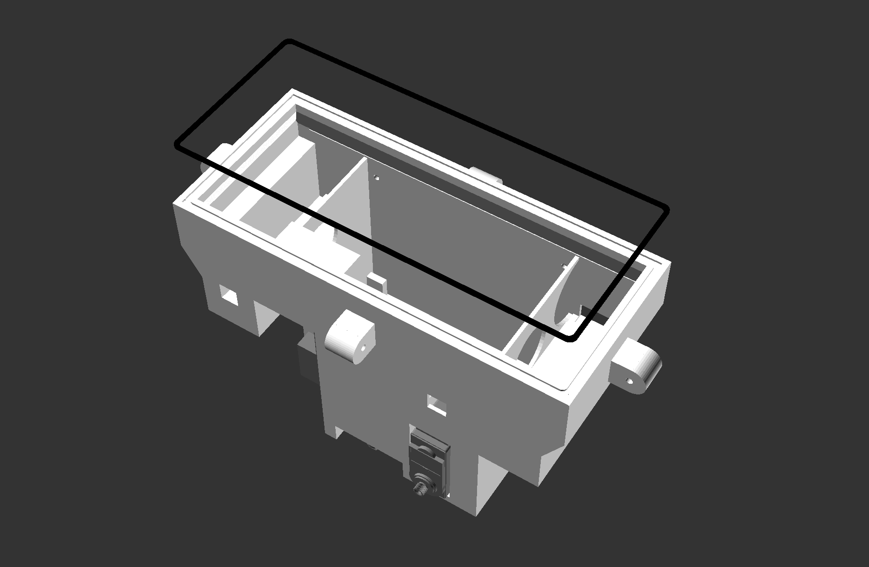
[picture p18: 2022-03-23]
Chamber_1/Build_Guide/Step 4_Construction_Manual_Animations/step_4a_5_animated.gif

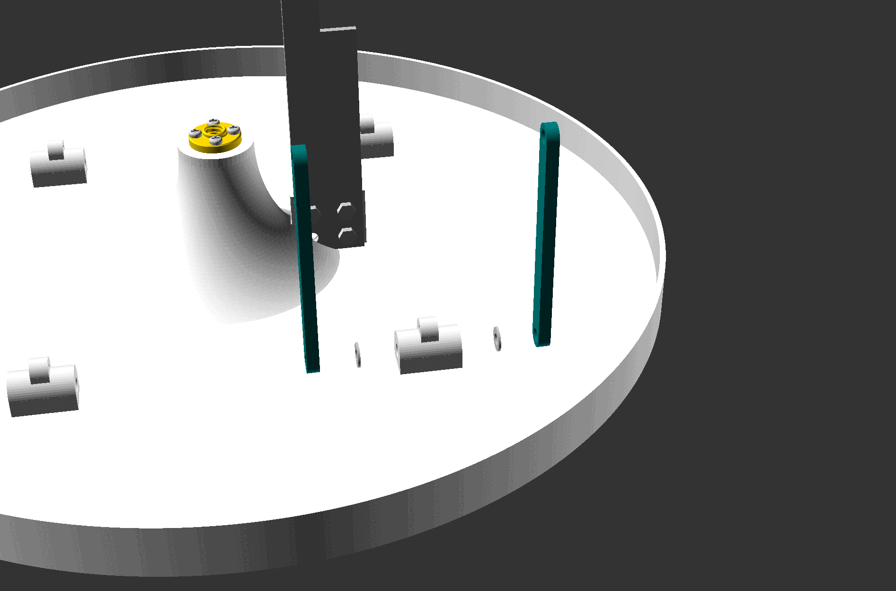
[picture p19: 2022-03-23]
Chamber_1/Build_Guide/Step 3_Construction_Manual_Animations/step_3a_3.gif

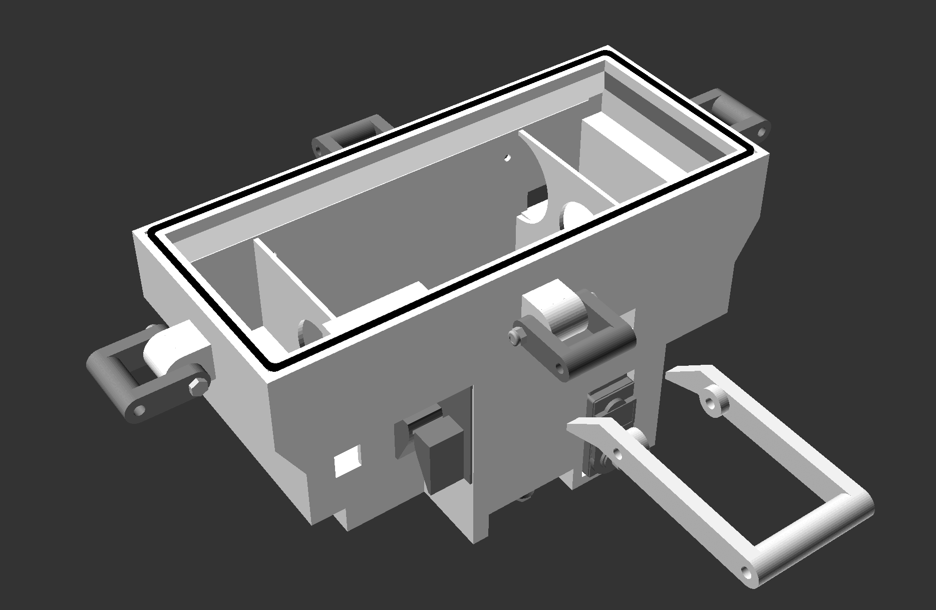
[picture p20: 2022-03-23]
Chamber_1/Build_Guide/Step 4_Construction_Manual_Animations/step_4a_7a_animated.gif

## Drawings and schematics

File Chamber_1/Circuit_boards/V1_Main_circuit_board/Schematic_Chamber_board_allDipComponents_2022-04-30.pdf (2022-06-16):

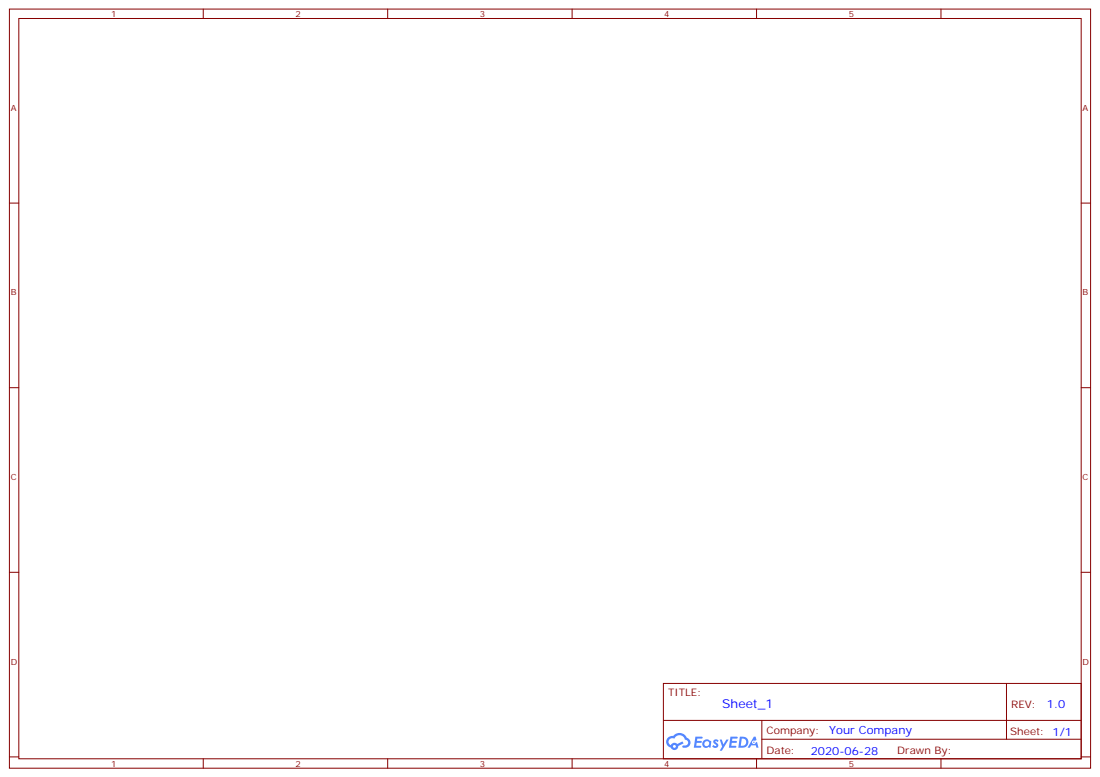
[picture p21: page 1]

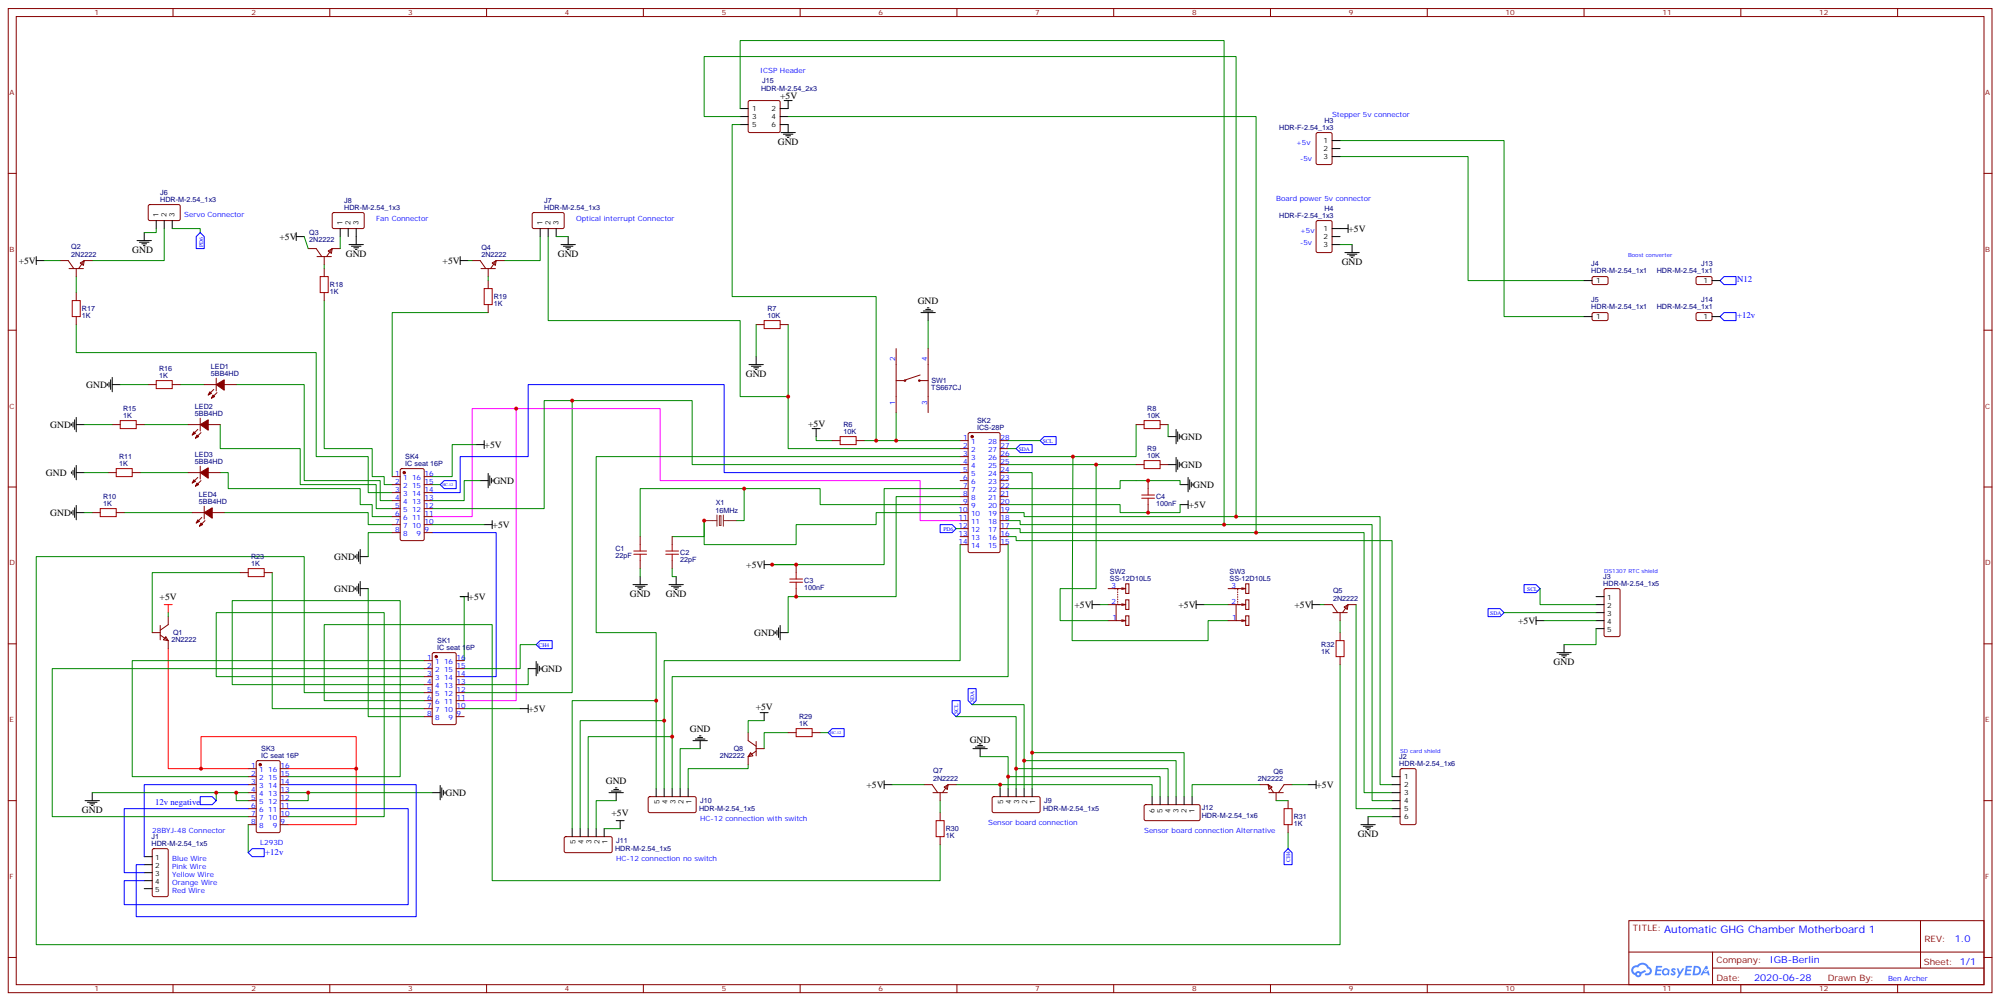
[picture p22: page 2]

Sensor board connection Alternative

TITLE: Automatic GHG Chamber Motherboard 1

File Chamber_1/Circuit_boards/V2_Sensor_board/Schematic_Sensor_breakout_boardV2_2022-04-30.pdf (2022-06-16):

CH4 1

CH4 2

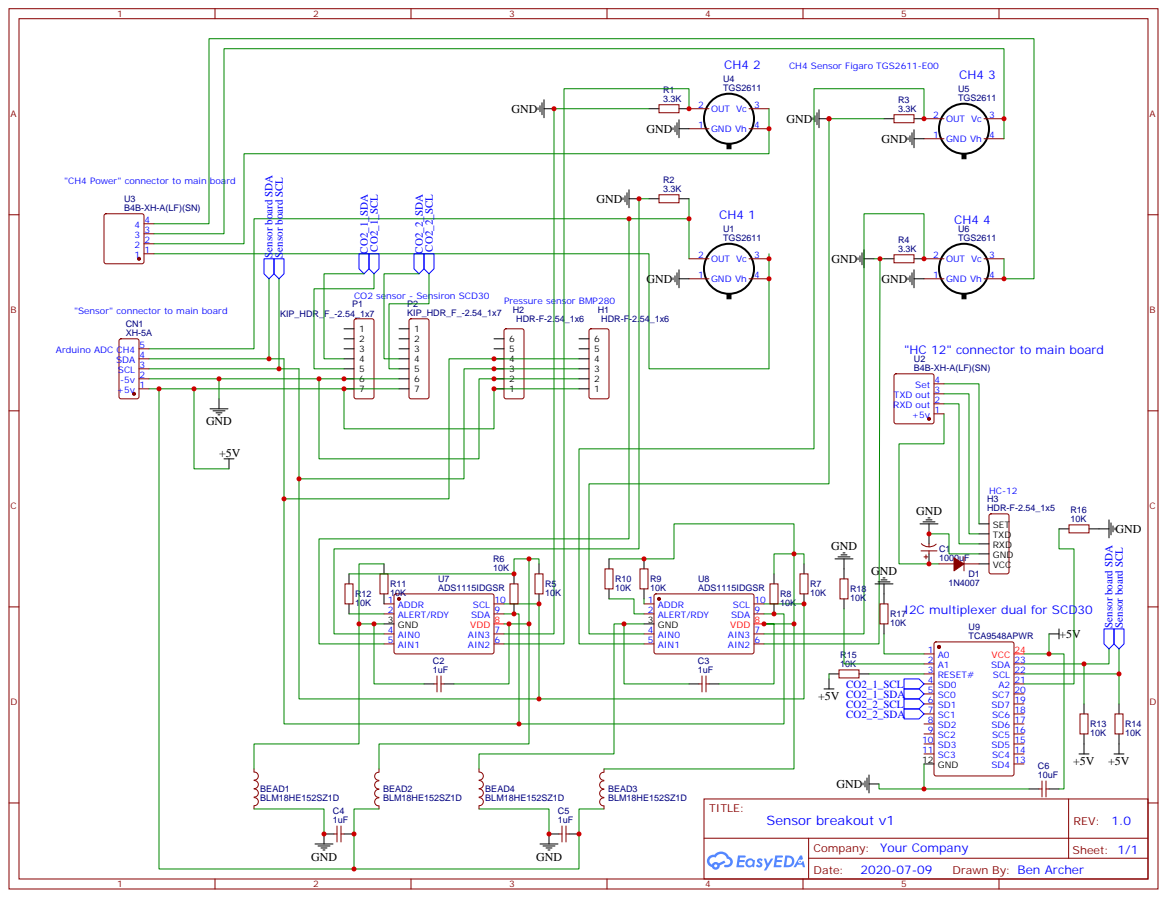
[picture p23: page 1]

"CH4 Power" connector to main board

"Sensor" connector to main board

Drawn By: Ben Archer

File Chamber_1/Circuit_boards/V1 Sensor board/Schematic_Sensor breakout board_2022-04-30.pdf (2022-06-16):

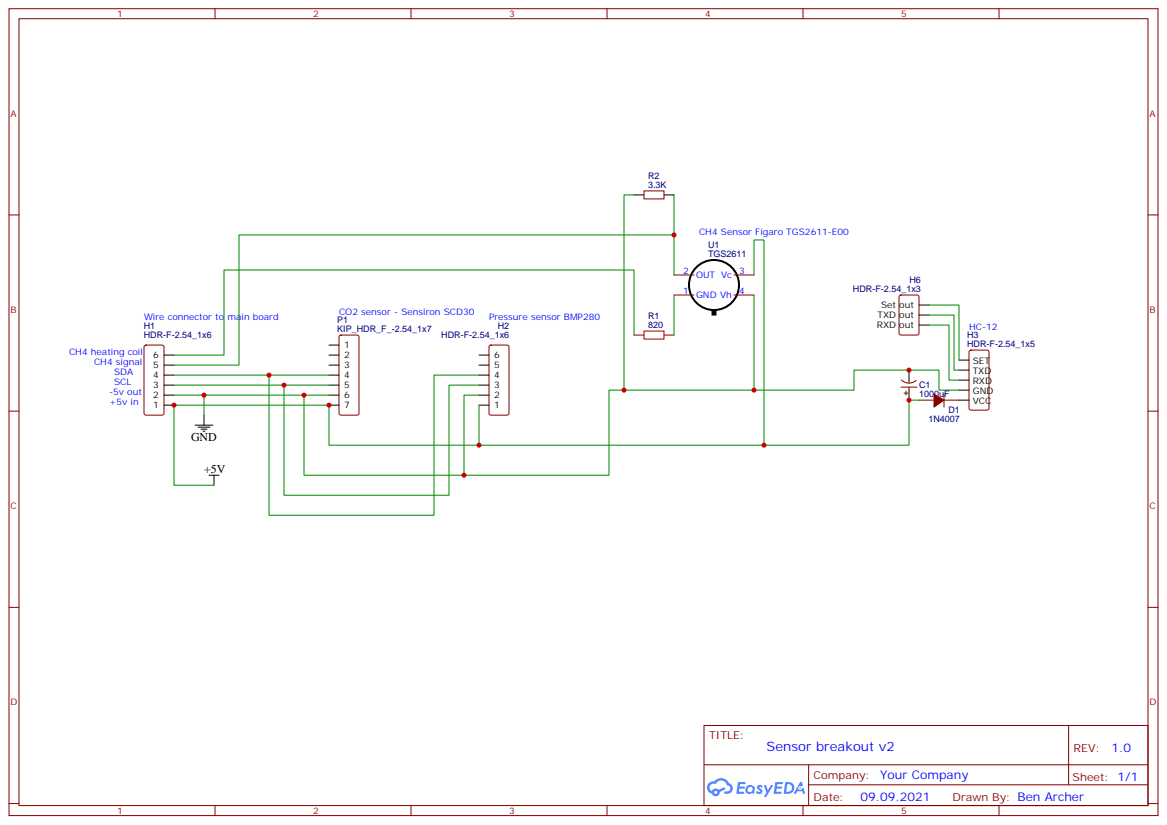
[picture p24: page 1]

Drawn By: Ben Archer

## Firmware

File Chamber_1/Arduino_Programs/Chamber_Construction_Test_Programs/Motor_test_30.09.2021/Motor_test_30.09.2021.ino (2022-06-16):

 

//House Keeping  ]

//strain sensor 
#include "HX711.h"
#define calibration_factor -1048.25  //calculated with the calibration sketch by sparkfun and 1kg weight on the chamber. Can be adjusted and checked in my custom example. 
const int LOADCELL_DOUT_PIN = 4;
const int LOADCELL_SCK_PIN = A2;
//int strain_start;
float strain_end;
HX711 scale;
    

//

#define peri  4
//sleep sketch variables 

int8_t buttonState=0;
#define USE_PROGMEM true
int8_t lastButtonState=0; 

//CH4 sensor
#define sensor A1

//pressure sensor 
#include <Wire.h>
#include "SparkFunBME280.h"
BME280 Pressure;

//CO2 sensor 

#include "SparkFun_SCD30_Arduino_Library.h" 
SCD30 airSensor;

//servo
//#include <Servo.h>
#include <ServoTimer2.h>  // the servo library
#define pawlPin  6
ServoTimer2 servoPawl;  

//int del = 2000;
//int time_time= 0; //variable to set stepper speed
//int steps = 100;
//int steps1 = 1;

//Servo myservo;  // create servo object to control a servo
// twelve servo objects can be created on most boards

int8_t pos = 0;    // variable to store the servo position

 

//intro for sd and rtc
#include <Time.h>
#include <DS1307RTC.h>

#include <SPI.h>
#include <SD.h>
File myFile;
File myFile1;
const char *monthName[12] = {
  "Jan", "Feb", "Mar", "Apr", "May", "Jun",
  "Jul", "Aug", "Sep", "Oct", "Nov", "Dec"
};

int8_t last_Day = 0;

//long alarmTime =0;
//long alarmTime2 =0;
 
tmElements_t tm;


//intro for HC-12
#include <AltSoftSerial.h>
AltSoftSerial mySerial; //TX, RX

#define setPin 1
boolean onOff = 0;
boolean led_bool = false;

int ExpectedCommand = 0 ; 
int LastCommand = 0;
int input = 0; 


int command1=0;
int command2=0;
int8_t counter2= 0; //counts the number of un read cycles in the radio manual mode, after 5 it takes a measurement thus ~ once every minute and a half. 

//mode switches

//#define mode_switch A3
#define strain_pin A3
//#define setup_switch A2

//intro code from sequence
#define endstop 0
#define SER_Pin 3   //pin 14 on the 75HC595
#define RCLK_Pin 2  //pin 12 on the 75HC595
#define SRCLK_Pin 7 //pin 11 on the 75HC595
//#define VMOT A0 //relay that controls the power supply for the motor 
#define STEP_PIN 5 //motor driver step pin (must be PWM compatible)
#define strain 4


//How many of the shift registers - change this
#define number_of_74hc595s 3 

//do not touch
#define numOfRegisterPins number_of_74hc595s * 8

boolean registers[numOfRegisterPins];



           


//set all register pins to LOW
void clearRegisters(){
  for(int8_t i = numOfRegisterPins - 1; i >=  0; i--){
     registers[i] = LOW;
  }
} 


//Set and display registers
//Only call AFTER all values are set how you would like (slow otherwise)
void writeRegisters(){

  digitalWrite(RCLK_Pin, LOW);

  for(int8_t i = numOfRegisterPins - 1; i >=  0; i--){
    digitalWrite(SRCLK_Pin, LOW);

    int8_t val = registers[i];

    digitalWrite(SER_Pin, val);
    digitalWrite(SRCLK_Pin, HIGH);

  }
  digitalWrite(RCLK_Pin, HIGH);

}

//set an individual pin HIGH or LOW
void setRegisterPin(int8_t index, int8_t value){
  registers[index] = value;
}

////////////////////////////////////////////////////////////////////
//declare variables for the motor pins
#define  DIR_PIN 9  // Blue   - 28BYJ48 pin 1 
#define  EN_PIN 10  // Pink   - 28BYJ48 pin 2 //Motor driver enable pin 
#define  MS1 11  // Yellow - 28BYJ48 pin 3
#define  MS2 12  // Orange - 28BYJ48 pin 4


#define  VIO 15 //motor driver +5v supply 
#define  fan 2
#define  servo_power 3
#define  tran 1 //optical end stop
#define  HC_12 0
#define  blue_LED 5
#define  white_LED 4
#define  ledPin 7//green led on board
#define  LedOff 6//red led
#define  sd_power 13
#define  sensorPower 14 //power for the other sensors
#define  ch4Power 8 //powers on ch4 heating element, which needs 1 minute to warm up before readings

#define VMOT 18
#define Vperi 16
#define motor_bank 22
                        











void setup() {
pinMode(STEP_PIN, OUTPUT);
pinMode(VMOT, OUTPUT);
digitalWrite(VMOT,LOW);

  
//Serial.begin(9600);
pinMode(10, OUTPUT); 
 pinMode(peri, OUTPUT);

//ch4 sensor
pinMode(sensor, INPUT);

//co2 sensor setup
Wire.begin(); 

//pressure sensor setup 
Pressure.setI2CAddress(0x76);

//servo setup
servoPawl.attach(pawlPin); 

  
//mode switch setup
//pinMode (mode_switch, INPUT);
pinMode (strain_pin, OUTPUT);
//pinMode (setup_switch, INPUT);


//Serial.begin(9600);
 pinMode(setPin, OUTPUT);
  mySerial.begin(9600);
  pinMode(ledPin, OUTPUT);
  
  digitalWrite(ledPin, led_bool);//turn LED on
  
  digitalWrite(setPin, HIGH);
  digitalWrite(ledPin, led_bool);//turn LED on
  //delay(1000);

  pinMode(endstop, INPUT);
  pinMode(SER_Pin, OUTPUT);
  pinMode(RCLK_Pin, OUTPUT);
  pinMode(SRCLK_Pin, OUTPUT);


  //reset all register pins
  clearRegisters();
  writeRegisters();
  
        
      setRegisterPin(EN_PIN, LOW);
      setRegisterPin(VIO, LOW);
                 writeRegisters();
                 delay(1000);
  
  //setRegisterPin(relay, LOW);
  
  
//Begin startup with all LEDS flashing on for for 1 second

//allLedflash(1000);

setRegisterPin(sd_power, HIGH);
setRegisterPin(sensorPower, HIGH);
setRegisterPin(tran, HIGH);
digitalWrite(strain_pin, HIGH);

writeRegisters(); 


 //function checking using led signals 

/*
/////////////////
//strain guage setup
scale.begin(LOADCELL_DOUT_PIN, LOADCELL_SCK_PIN);
   delay(50);

   for(;;){
 if (scale.is_ready()) {
allOkayLED (500); 
break;
  } else {
     notOkayLED(200);
     scale.begin(LOADCELL_DOUT_PIN, LOADCELL_SCK_PIN);
   delay(50);
  }}

  
allLedflash(1000);

*/

for(int8_t y = 1; y <= 5; y++){
allLedflash(200); }




//close_sequence ();
//open_sequence ();
//sensors_read (2,1);
/*
 setRegisterPin(ch4Power, HIGH);

   writeRegisters();
   delay(5000);
  setRegisterPin(ch4Power, LOW);

   writeRegisters();*/

   digitalWrite(strain_pin, LOW);

      setRegisterPin(sd_power, LOW);
setRegisterPin(sensorPower, LOW);
  setRegisterPin(VIO, LOW);
setRegisterPin(fan, LOW);
  setRegisterPin(servo_power, LOW);
setRegisterPin(tran, LOW);
  setRegisterPin(HC_12, LOW);
setRegisterPin(fan, LOW);

writeRegisters(); 
//digitalWrite(setPin, LOW);
//Serial.begin(9600);
}


void loop() {
  // put your main code here, to run repeatedly:

setRegisterPin(motor_bank, HIGH);

writeRegisters(); 

delay(1000);

setRegisterPin(motor_bank, LOW);

setRegisterPin(VMOT, HIGH);//set the motor voltage high first 

writeRegisters(); 

writeRegisters(); 





delay(1000);//pause to make sure the relay switch has activated, long time because it is mechanical 

      setRegisterPin(VIO, HIGH); //turning on the +5v for the motor driver VIO after the VMOT
                 writeRegisters();

                 delay(500); //a little time for the system to react

      setRegisterPin(DIR_PIN, HIGH); //DIR LOW = lid down  
      setRegisterPin(MS1, HIGH);  //MS1 High and Peristaltic_pump LOW = fast steps mode 
      setRegisterPin(MS2, LOW);
      writeRegisters();

    setRegisterPin(EN_PIN, HIGH); //Enable the motor just before movement  
                 writeRegisters();


      
for(int i=0; i<450; i++){ //stepping loop was 450 but changed to 200 for chamber 28.07.2021
  //make steps
  digitalWrite(STEP_PIN, HIGH);
  delay(15);
  digitalWrite(STEP_PIN, LOW);
  delay(15);
}

    setRegisterPin(EN_PIN, LOW); //Enable the motor just before movement  
                 writeRegisters();

                 delay(1000);

        setRegisterPin(DIR_PIN, LOW); //DIR LOW = lid down  
      setRegisterPin(MS1, HIGH);  //MS1 High and Peristaltic_pump LOW = fast steps mode 
      setRegisterPin(MS2, LOW);
      writeRegisters();     

        delay(500);
        
        setRegisterPin(EN_PIN, HIGH); //Enable the motor just before movement  
                 writeRegisters();   


      
for(int i=0; i<450; i++){ //stepping loop was 450 but changed to 200 for chamber 28.07.2021
  //make steps
  digitalWrite(STEP_PIN, HIGH);
  delay(15);
  digitalWrite(STEP_PIN, LOW);
  delay(15);
}

        

   setRegisterPin(EN_PIN, LOW); //Disable the motor first  
            writeRegisters();

delay(500);

                 setRegisterPin(VIO, LOW); //motor driver +5V turned off first, before motor voltage
                 setRegisterPin(VMOT, LOW);// 
                  writeRegisters();  

delay(9000);

                    

}





void allLedflash (int x){
 setRegisterPin(blue_LED, HIGH); 
 setRegisterPin(white_LED, HIGH);
 setRegisterPin(ledPin, HIGH); 
 setRegisterPin(LedOff, HIGH); 
 writeRegisters();
 delay(x);
 setRegisterPin(blue_LED, LOW); 
 setRegisterPin(white_LED, LOW);
 setRegisterPin(ledPin, LOW); 
 setRegisterPin(LedOff, LOW); 
 writeRegisters();
 delay(x);


}

void allOkayLED (int x){

 for(int8_t i=1;i<=3;i++){ 
 setRegisterPin(ledPin, HIGH);  
 writeRegisters();
 delay(x);
 setRegisterPin(ledPin, LOW); 
 writeRegisters();
 delay(x);}


}

void notOkayLED (int x){

 
 setRegisterPin(LedOff, HIGH); 
 writeRegisters();
 delay(x);
 setRegisterPin(LedOff, LOW);
 writeRegisters();
 delay(x);


}



void radio_report (int x){

  //sd power on 
   setRegisterPin(sd_power, HIGH);
   setRegisterPin(sensorPower, HIGH);
   writeRegisters();

   delay(200);
//
//   while (!SD.begin()) { //whilst the sd is not okay, the green and red led are turned on alternately
//           delay(2000);    
//notOkayLED(500);


//}


////read endstop state////
   setRegisterPin(tran, HIGH);
   writeRegisters();
  delay(50);
  int8_t lid_position = digitalRead(endstop);
  delay(100);
  setRegisterPin(tran, LOW);
   writeRegisters();
                 

   tmElements_t tm;
   RTC.read(tm);
   
char data[12];
int8_t* DAY = (tm.Day);
int8_t* MONTH = (tm.Month);
int* YEAR = (tm.Year)+1970-2000;

char data2[12];
int* seconds = (tm.Second);
int* minutes = (tm.Minute);
int* hours = (tm.Hour);

  sprintf(data, "%u_%u_%u", DAY,MONTH,YEAR);
  sprintf(data2, "%u:%u:%u", hours,minutes,seconds);
  
   myFile1 = SD.open((F("Status.txt")), FILE_WRITE); //not sure if this f will work
   if (myFile1) {
    //Serial.print("Writing to test.txt...");
    myFile1.print(data);
    myFile1.print(F(", "));
    myFile1.print(data2);
    myFile1.print(F(", "));
    myFile1.print(x);
    myFile1.print(F(", "));
    myFile1.print(F("Optical_state: "));
    myFile1.println(lid_position);
    // close the file:
    myFile1.close();}
    delay(100);

   setRegisterPin(sd_power, LOW);
   setRegisterPin(sensorPower, LOW);
   writeRegisters();
}

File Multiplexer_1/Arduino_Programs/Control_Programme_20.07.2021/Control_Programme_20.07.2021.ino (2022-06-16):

//WInd sensor feedback loop
//this sketch is a safety to make sure the LGR does not break, e.g. when in manual mode forgetting to switch the two solenoids on at once 

//To begin with, the LGR should not be plugged into the valve changer module. , so as to make sure the LGR begins.
//once a conformation signal is recieved from the valve changer board, the relay is opened, turning the LGR on. 
//Once the LGR begins to pump air, plug it back into the valve changer. This should turn off the LED as confirmation that air flow is detected 
//now the circuit is in protection mode, the next time no air flow is detected the system will hard shut down the LGR .

//pull sdo pin on pressure sensor high to use 0x77 address on the pressure sensor. Pull it low for the 0x76 address 

//20.07.2021 edit to include the pressure control setting in the manual chamber method 
//will put the pressure check in the loop with the lgr off switch loop check. and set the lgr pressure at the start after the off switch has been selected once





/*Wind Sensor Signals    Arduino
 GND                    GND
 +V                     5V
 RV                     A1    // modify the definitions below to use other pins
 TMP                    A0    // modify the definitions below to use other pins
 

 
 Hardware setup:
 Wind Sensor is powered from a regulated five volt source.
 RV pin and TMP pin are connected to analog innputs.
 
 */
 #include "SparkFunBME280.h"
BME280 Pressure;
BME280 Pressure2;

#include <Time.h>
#include <DS1307RTC.h>
#include <Wire.h>
#include <SPI.h>
#include <SD.h>
File myFile;
File myFile1;
const char *monthName[12] = {
  "Jan", "Feb", "Mar", "Apr", "May", "Jun",
  "Jul", "Aug", "Sep", "Oct", "Nov", "Dec"
};
 
#define analogPinForRV    A3   // change to pins you the analog pins are using
#define analogPinForTMP   A2


int lgr_relay = 6;

int rst = 5; 

int mode_signal= 8; 

int lgr_control= 9; 

int lgr_on_led= 2; 

int lgr_off_led = 3; 

int rv = A3; 

int tmp = A2; 

int lgr_manual_switch = A1; 



int switch_state; 

// to calibrate your sensor, put a glass over it, but the sensor should not be
// touching the desktop surface however.
// adjust the zeroWindAdjustment until your sensor reads about zero with the glass over it. 

const float zeroWindAdjustment =  .5; // negative numbers yield smaller wind speeds and vice versa.

int TMP_Therm_ADunits;  //temp termistor value from wind sensor
float RV_Wind_ADunits;    //RV output from wind sensor 
float RV_Wind_Volts;
unsigned long lastMillis;
int TempCtimes100;
float zeroWind_ADunits;
float zeroWind_volts;
float WindSpeed_MPH;


int TMP_Therm_ADunits2;  //temp termistor value from wind sensor
float RV_Wind_ADunits2;    //RV output from wind sensor 
float RV_Wind_Volts2;

int TempCtimes100_2;
float zeroWind_ADunits_2;
float zeroWind_volts_2;
float WindSpeed_MPH2;



int TMP_Therm_ADunits3;  //temp termistor value from wind sensor
float RV_Wind_ADunits3;    //RV output from wind sensor 
float RV_Wind_Volts3;

int TempCtimes100_3;
float zeroWind_ADunits_3;
float zeroWind_volts_3;
float WindSpeed_MPH3;



int TMP_Therm_ADunits4;  //temp termistor value from wind sensor
float RV_Wind_ADunits4;    //RV output from wind sensor 
float RV_Wind_Volts4;

int TempCtimes100_4;
float zeroWind_ADunits_4;
float zeroWind_volts_4;
float WindSpeed_MPH4;



int TMP_Therm_ADunits5;  //temp termistor value from wind sensor
float RV_Wind_ADunits5;    //RV output from wind sensor 
float RV_Wind_Volts5;

int TempCtimes100_5;
float zeroWind_ADunits_5;
float zeroWind_volts_5;
float WindSpeed_MPH5;




void setup() {
//pressure sensor setup 
  Serial.begin(9600);
  delay(100);
   Serial.println ("begin");
Pressure2.setI2CAddress(0x77); // inlet pressure sensor
 Serial.println ("...");
Pressure.setI2CAddress(0x76); // outlet pressure sensor
 Serial.println ("...");
//Serial.println ("Address");
  while (Pressure.beginI2C()==false){
    delay(50);
    Serial.println("pressure sensor 1 false");
    delay(50);    
  }
  
  Serial.println ("pressure 1 okay");
    while (Pressure2.beginI2C()==false){
       delay(50);    
    Serial.println("pressure sensor 2 false");
     delay(50);
  }

  Serial.println ("pressure 2 okay");
  
  pinMode(lgr_relay, OUTPUT);
  pinMode(rst, OUTPUT);
  pinMode(mode_signal, INPUT);
  pinMode(lgr_control, INPUT);
  pinMode(lgr_on_led, OUTPUT);
  pinMode(lgr_off_led, OUTPUT);
  pinMode(rv, INPUT);
  pinMode(tmp, INPUT);
  pinMode(lgr_manual_switch, INPUT);

  digitalWrite(lgr_relay, LOW);
   digitalWrite(lgr_off_led, HIGH);
   digitalWrite(lgr_on_led, LOW);
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

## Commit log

2022-03-24 Chamber_1 update
2022-03-29 Arduino programs upload
2022-06-16 Add files via upload
    Still under work. Needs electrical installation and testing information, 3d printing support removal guide and information on cutting aluminium bars / floats.
